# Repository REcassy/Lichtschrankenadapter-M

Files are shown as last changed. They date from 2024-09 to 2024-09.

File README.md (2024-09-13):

# Lichtschrankenadapter-M
Open sensor for use with any standard light barrier on a Mobile Cassy.

This repo is under active development, so schematic and pcb files may not match always. Use the current release for production: https://github.com/REcassy/Lichtschranke-M/releases/tag/v1.0

## Compatible barriers
The Mobile Cassy pulls J2 to 5V (barrier 1) and J3 to 3.7V (barrier 2). Your light barrier needs to pull that down to less than 2V to register an event. A photo-transistor is optimal for that. You barrier can make use of +5V / GND jacks to power the light source. You should try to use as little current as possible to not put a strain on the Mobile Cassy's batteries, but anything up to 100mA seems to be acceptable.

Use at your own risk - especially drawing power. There is no public information on current limiting or fuses inside the Mobile Cassy. Always prefer LED to incandescent bulbs.

## Testing
For testing I included an Arduino simulator code. For this you need to connect the I<sup>2</sup>C pins of your Arduino (e.g. on a Uno Pins the upper right ones) to the I<sup>2</sup>C pins of the Cassy Mini-DIN interface (SDA: 1 and SCK: 5) as well as pin 7 of the Arduino (change this, if this is no digital out on your Arduino) to Mini-DIN pin 2.

## Programming your ATtiny25
The included ino file is intended for use with the Arduino IDE and any Arduino as an ISP Programmer. You need to:
* load the ISP sketch from the Arduino IDE (File->Examples->11. ArduinoISP) onto your Arduino Uno
* install ATTinyCore (https://github.com/SpenceKonde/ATTinyCore) as a board manager into your Arduino IDE 
* connect the Arduino to the ATTiny according to this graphic:

Untitled Sketch_Steckplatine

* when using other ATTiny chips check the datasheet or the ATtinyCore [repo][attiny-boards]
* set Tools->Board to ATtinyCore-> "ATtiny25/45/85 (no bootloader)"
* set Tools->Chip to ATtiny25
* set Tools->Programmer to "Arduino as ISP"
* use Tools->Burn Bootloader to set the appropriate E-Fuses in your ATtiny (only necessary with a brand new ATtiny)
* use Sketch->Upload Using Programmer

There are of course countless other ways to program your ATtiny. You can find the .hex file in the ATtiny directory.

## Schematic and PCB
The schematic and PCB files were created with KiCAD.

Be aware that earlier photos on my blog show a switched J4/J5 label (GND and 5V) as well as an incorrectly polarized C2.

The PCB file ending in "-tube" is used with brass tubes (see BOM) as connectors the one ending in "-jack" with ready made 4mm jacks.

Below you can see both boards fully populated:

grafik

## BOM
You need the following (given in brackets are Reichelt ordering numbers for reference):

| Part Label  | Description | Form factor | Reichelt number |
| ------------- | ------------- | ------------- | ------------- |
| U1  |  ATiny25 | DIP-8 | ATTINY 25-20 PU |
| U2 | USBLC6 | SOT-23-6 |  USBLC6-2SC6 |
| C1, C3 | 50V 100nF ceramic cap | 1206 |  WAL 1206B104K500 |
| C2 | 50V 10µF electrolytic cap | RM2,5 |  SU-A 10U 50|
| R1, R2 | 0,25W 5K1 resistor | 0207 |  1/4W 5,1K |
| J1 | Mini-Din 6 connector | N/A | EB-DIOS M06 |
| J2-J5 | 4mm ID, 5mm OD brass tube | N/A | N/A |
| J2-J5 | 4mm laboratory jacks | N/A | SEP 2610 F48  |

choose either J2-J5 option and the appropriate PCB design.

## Gerber and drill files
The gerber and drill files were exported from KiCAD and are ready to be sent to any PCB manufacturer of your choice. The PCB design features no vias. Any standard double sided process will suffice.
Please choose the correct set of files for your desired jacks.

Below are the renderings for both variants:

     

## 3D-printed case
A 3D printable case is currently in development.

[attiny-boards]: https://github.com/SpenceKonde/ATTinyCore/blob/v2.0.0-devThis-is-the-head-submit-PRs-against-this/avr/extras/ATtiny_x5.md

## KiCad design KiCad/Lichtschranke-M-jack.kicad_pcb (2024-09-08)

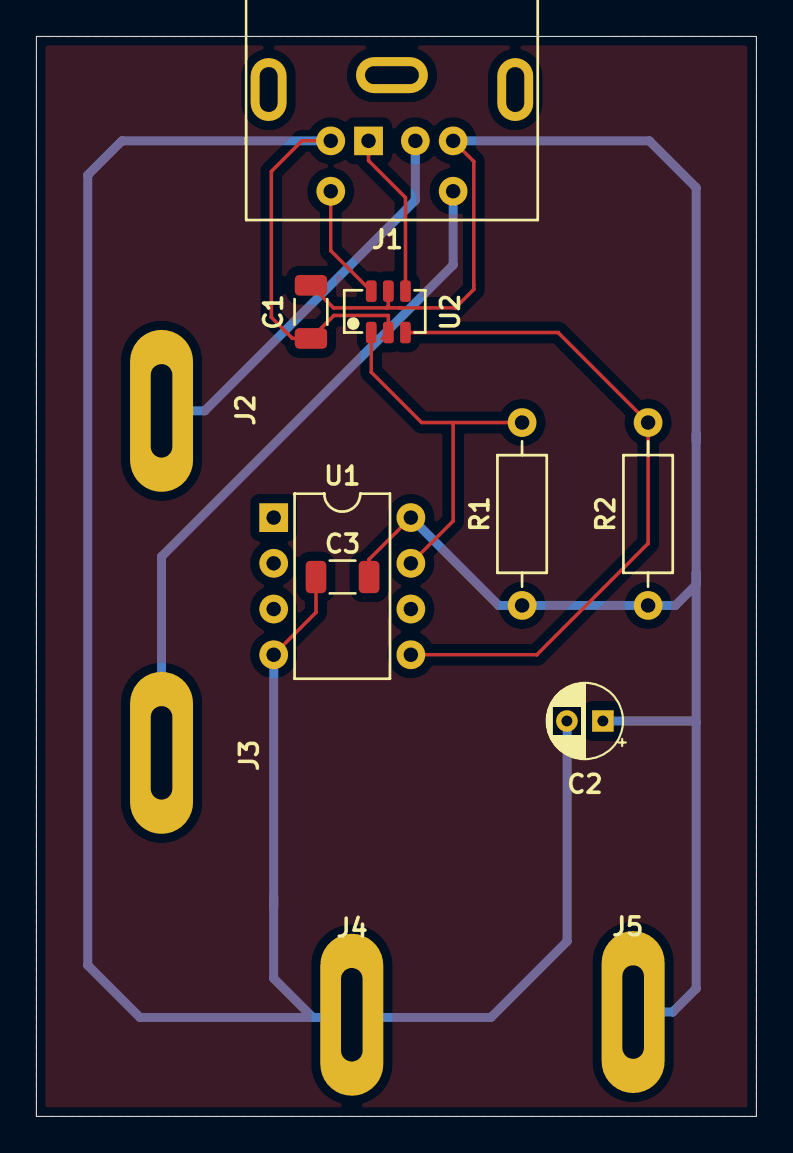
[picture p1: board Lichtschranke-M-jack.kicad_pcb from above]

Board: 2 copper layers, 40.0 x 60.0 mm, 12 parts (0 on the bottom side), 8 nets.

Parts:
C1, C3: C; C_1206_3216Metric
C2: C_Polarized; CP_Radial_D4.0mm_P2.00mm
J1: Mini-DIN-6; Connector_Mini-DIN_Female_6Pin_2rows
J2, J3, J4, J5: Conn_01x01_Socket; Banana-Slot
R1, R2: R; R_Axial_DIN0207_L6.3mm_D2.5mm_P10.16mm_Horizontal
U1: ATtiny25-20P; DIP-8_W7.62mm
U2: USBLC6

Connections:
+5V: C1.1, C2.1, C3.2, J1.4, J5.1, R1.1, R2.1, U1.8 (VCC), U2.5 (VBus)
E: J1.2, J2.1
F: J1.6, J3.1
GND: C1.2, C2.2, C3.1, J1.3, J4.1, U1.4 (GND), U2.2 (GND)
unnamed: R2.2, U1.5 (AREF/PB0), U2.3 (I/O2)
unnamed: R1.2, U1.7 (PB2), U2.1 (I/O1)
SCK: J1.5, U2.6 (I/O1)
SDA: J1.1, U2.4 (I/O2)

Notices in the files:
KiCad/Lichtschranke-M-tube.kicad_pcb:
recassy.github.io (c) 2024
